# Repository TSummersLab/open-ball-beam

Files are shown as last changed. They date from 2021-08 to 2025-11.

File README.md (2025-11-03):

<div align="center">

</div>

# OBB: Open Ball & Beam

[**Hardware**](#hardware)
| [**Software**](#software)
| [**Mathematics**](#mathematics)
| [**Contributors**](#contributors)

## What is OBB?

OBB is *control science for everyone*.

1. A low-cost, open-source hardware and software platform.
2. For research, teaching, and self-guided instruction in data-driven control.
3. An open-loop neutrally stable dynamical system that is nontrivial to control.

## Why OBB?

[Existing educational control systems](docs/ALTERNATIVES.md) are often

1. Prohibitively expensive (cost thousands of USD)
2. Use proprietary hardware and software
   - Development knowledge is not transferrable to other systems.

OBB offers a viable alternative

1. OBB is cheap enough for most individuals and labs.
2. OBB uses open-source and widely available hardware and software.

OBB encourages users to get their hands dirty!

1. Redesign custom 3D parts
2. Create new & improved controllers
3. Try out reinforcement learning algorithms

# Hardware

## Parts list

See [`parts_list.xlsx`](hardware/parts_list.xlsx) for a list of parts to purchase and to kit out a single OBB unit.

## CAD models

CAD models for 3D printing are provided in the [`cad`](hardware/cad) directory.

- [STEP files](hardware/cad/step) (portable format), suitable for 3D printing.
- [PTC Creo files](hardware/cad/creo) (native format), suitable for viewing and redesign in PTC Creo.
  - The full assembly [`ballbeam.asm`](hardware/cad/creo/ballbeam.asm) may be opened in Creo. Working kinematic joints are provided so the movement can be interacted with via dragging.

## Assembly and setup

See the [Assembly and Setup Guide](docs/OBB_Assembly_and_Setup_Guide/OBB_Assembly_and_Setup_Guide.pdf) for instructions on how to assemble an OBB unit.

<div align="center">
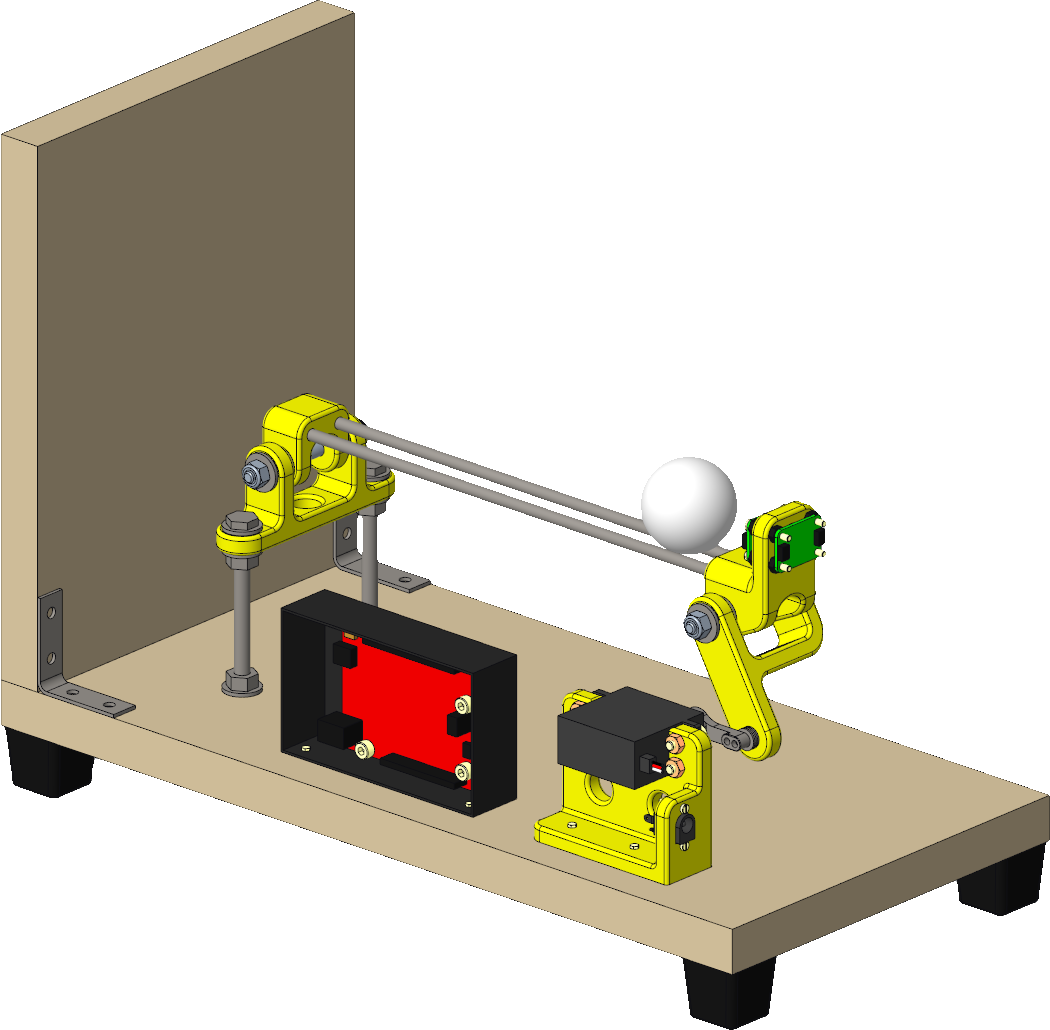
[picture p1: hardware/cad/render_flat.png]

&nbsp; &nbsp; &nbsp; &nbsp;
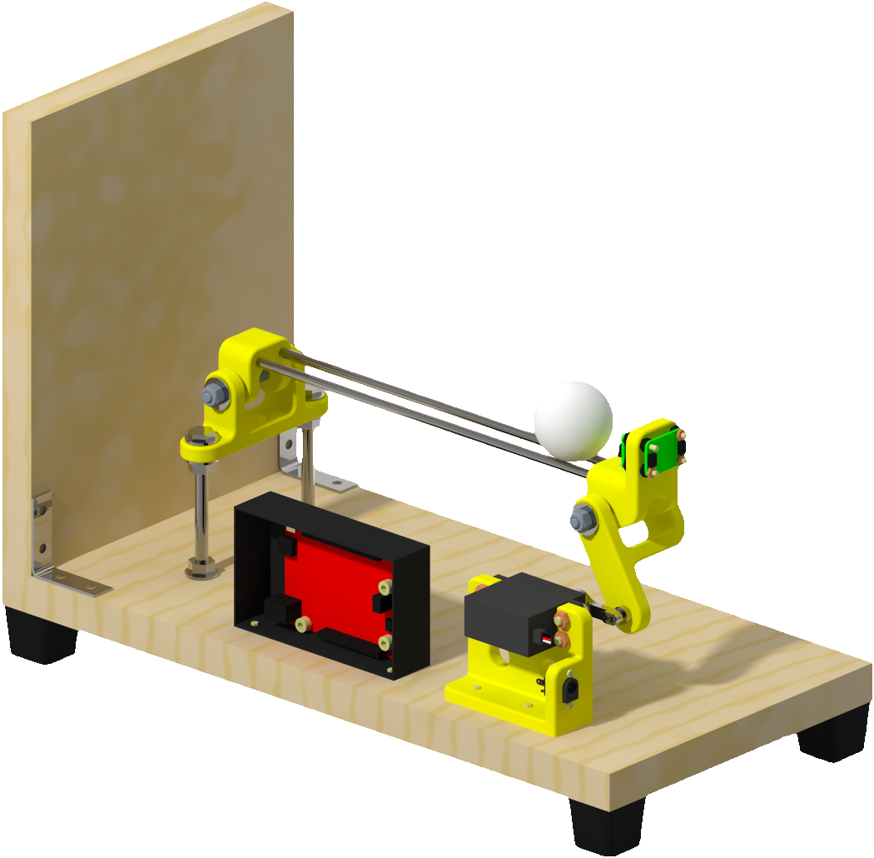
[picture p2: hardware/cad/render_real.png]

&nbsp; &nbsp; &nbsp; &nbsp;
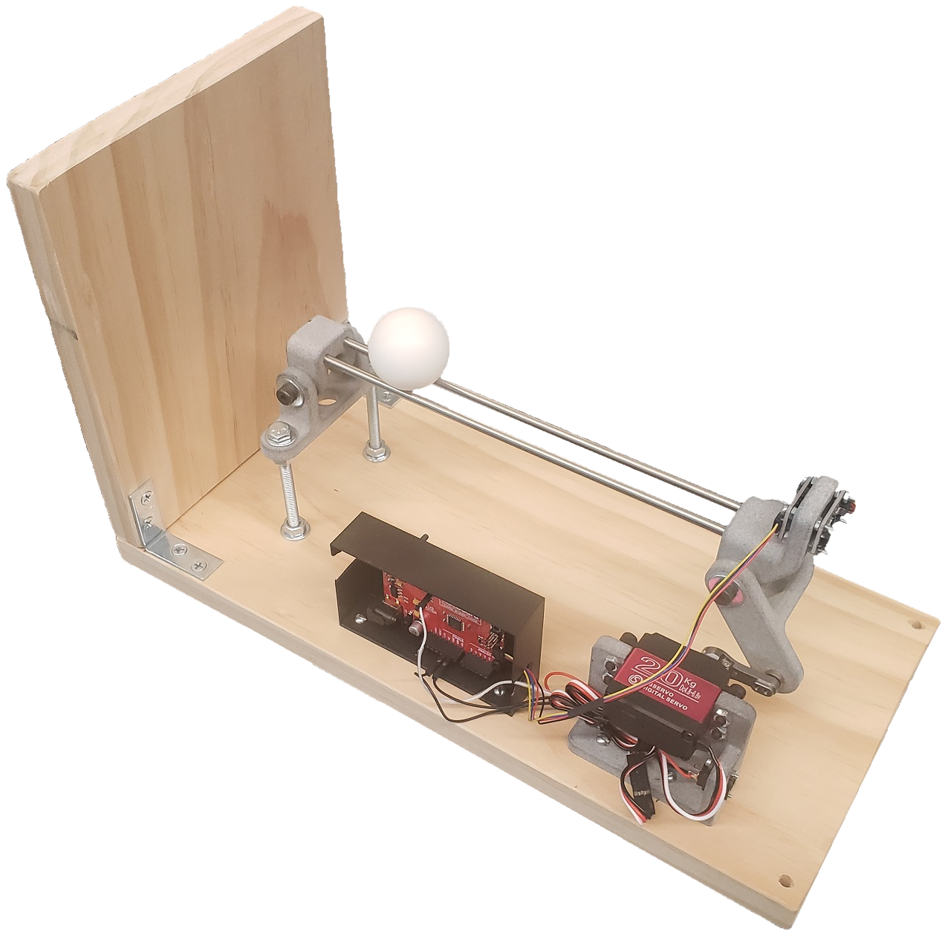
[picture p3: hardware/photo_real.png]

</div>

# Software

## Development info

OBB was developed and tested on 64-bit Windows 10 using Anaconda environments, but should work on other platforms as well e.g. macOS & Linux.

## Features

OBB ships with the following software features.

### Control schemes

- Proportional-integral-derivative (PID)
- Linear quadratic regulator (LQR) with integral control
- Model predictive control (MPC) with integral control
- Anti-windup for integral control

### Observation processing schemes

- Exponential smoothing
- Linear quadratic state estimation (Kalman filter)

### Convenience features

- Ball removal detection

### OpenAI Gym environments

OBB ships with environments compatible with [OpenAI Gym](https://gym.openai.com/) (requires Gym installation)

- Continuous action-space environment `BallBeamContinuousEnv`
- Discrete action-space environment `BallBeamDiscreteEnv`
- Option to use simulator (with fast visualizer) or the actual physical hardware

Try out reinforcement learning algorithms e.g. those from [OpenAI Spinning Up](https://spinningup.openai.com/en/latest/) in simulation or on a real-world physical system!

## Setup

### Arduino

#### Dependencies

- [Arduino IDE](https://www.arduino.cc/en/software)
- [Servo library](https://www.arduino.cc/reference/en/libraries/servo/)
- [Polulu VL53L0X library](https://github.com/pololu/vl53l0x-arduino)
- [Adafruit_LSM6DS](https://github.com/adafruit/Adafruit_LSM6DS)
- [BasicLinearAlgebra](https://www.arduino.cc/reference/en/libraries/basiclinearalgebra/)

1. Install the [Arduino IDE](https://www.arduino.cc/en/software)
2. Install the following libraries from the `Manage Libraries...` dialog in the Arduino IDE
    - [Servo](https://www.arduino.cc/reference/en/libraries/servo/) (may be installed already with the Arduino IDE)
    - [Polulu VL53L0X](https://github.com/pololu/vl53l0x-arduino)
        - Search for `VL53L0X`
        - Be sure to use the Polulu library and NOT the Adafruit Library (regardless of whether the Polulu or the Adafruit physical hardware is used)
    - [Adafruit_LSM6DS](https://github.com/adafruit/Adafruit_LSM6DS)
        - Search for `Adafruit LSM6DS`
        - Select `Install All` if prompted
    - [BasicLinearAlgebra](https://www.arduino.cc/reference/en/libraries/basiclinearalgebra/)
        - Search for `BasicLinearAlgebra`

### Python

It is recommended to use [virtualenv](https://docs.python.org/3/library/venv.html) to create a separate environment to install OBB and its dependencies.

1. Open a terminal / command prompt
2. Create a new environment
3. Activate the desired environment
4. Install the dependency packages
    - ```pip install -r requirements.txt```

#### OBB Installation

1. Navigate to the root level directory of this package.
2. Run the command `pip install -e .`
    - NOTE: The `-e` option is very important! This is what tells pip to install in "editable mode", so that changes you make to scripts actually take effect when you run them! Read the [official pip docs](https://pip.pypa.io/en/stable/topics/local-project-installs/#editable-installs) for more details.

#### Development

##### Pre-commit

Run

```bash
pre-commit run --all-files
```

to run all pre-commit hooks, including style formatting and unit tests.

##### Package management

Update [`requirements.in`](requirements.in) with new direct dependencies.

Then run

```bash
pip-compile requirements.in
```

to update the [`requirements.txt`](requirements.txt) file with all indirect and transitive dependencies.

Then run

```bash
pip install -r requirements.txt
```

to update your virtual environment with the packages.

If necessary, also add the type hints package to the `additional_dependencies` for `mypy` in [`.pre-commit-config.yaml`](.pre-commit-config.yaml) so that `mypy` knows about the type hints (often required for less popular packages).

### General setup (cross-platform Arduino <--> Python)

1. Baud rate
    - A baud rate of 115200 is used throughout the project.
    - When using `Tools` -> `Serial Monitor` or `Serial Plotter` make sure to use 115200 baud rate.

2. COM port
    - Determine the COM port that your Arduino is attached to
        - e.g. use Device Manager in Windows
    - In [`hardware_configurator.py`](ballbeam/configurators/hardware_configurator.py) change `PORT` to `COM#` as appropriate.

3. Servo and sensor calibration coefficients
    - Run [`servo_calibrator.py`](ballbeam/calibrators/servo_calibrator.py) and [`sensor_calibrator.py`](ballbeam/calibrators/sensor_calibrator.py)
    - Copy the printed coefficients into [`constants.cpp`](ballbeam/arduino/interface/src/constants.cpp)

## APIs

There are two APIs that offer comparable functionality:

1. [**Arduino API**](#arduino-api)
2. [**Python API**](#python-api)

### Arduino API

In the Arduino API, all processing (e.g. control and state estimation) occurs locally on the Arduino board. No serial connection to a host computer is strictly required during system operation; a serial connection is required only for uploading programs and for monitoring system operation through the Serial Monitor and Serial Plotter.

The benefit of the Arduino API is that no host computer is required to run the system.
In this configuration, only power to the Arduino (e.g. over the USB cable) is necessary, so the system is more portable and be run from any location with power outlets.
MPC control is currently not available in the Arduino API.

#### Usage

##### Arduino

1. Upload [`interface.ino`](ballbeam/arduino/interface/interface.ino) to the Arduino.
2. Start the `Tools` -> `Serial Plotter` to monitor the various signals in the system.

### Python API

In the Python API, the majority of processing occurs on the host computer and the Arduino acts as a simple client, sending raw measurement information and receiving actuator commands. A stable serial connection is required throughout system operation to maintain stability.

The benefit of the Python API is that the full computing power of the host computer can be used to control the system.
In particular, the more computationally intensive MPC strategy can be used.

#### Setup

In order to use the MPC controller, the solver code must be generated with

```bash
python configurators/controller/mpc/design.py
```

#### Usage

##### Arduino

1. Upload [`client.ino`](ballbeam/arduino/interface/client.ino) to the Arduino.

##### Host computer

1. Adjust all the configurable parameters in the [`*_configurator.py`](ballbeam/configurators) files as needed.
     - Set the `system_type` variable to `'Simulator'` in [`interface_configurator.py`](ballbeam/configurators/interface_configurator.py) first to ensure proper functioning in the simulator before attempting to run on the physical hardware.
2. Run [`python configurators.py`](ballbeam/configurators/configurators.py) to run all configurators.
3. Run [`python main.py`](ballbeam/common/interface.py) to start the interface (without running configurators).
    - Alternatively, run [`python main.py --configure`](ballbeam/main.py) to run the configurators as well as start the interface.

## Mathematics

An technical write-up describing the [mathematics](docs/OBB_Mathematics/OBB_Mathematics.pdf) behind the software is available.
Note that this document is still in development.

# Contributors

- Original author: [Benjamin Gravell](https://github.com/BenGravell)
- Testing and improvements: [Sleiman Safaoui](https://github.com/The-SS) and [Karthik Ganapathy](https://github.com/Klickeazy)

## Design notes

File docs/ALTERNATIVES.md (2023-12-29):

# Alternative Ball & Beam systems

## Quanser Ball and Beam

- Commercial product available from <https://www.quanser.com/products/ball-and-beam/> .
- Price not publicly available, but indications are that the cost runs in the several thousand dollar range. <https://ftp.esat.kuleuven.be/stadius/barrero/cacsd/www%20and%20mails/EDU_Pricing.pdf>
- Proprietary control software, tethered to a company for support and under-the-hood knowledge.

## BOBShield

Recently BOBShield was proposed:

- <https://ieeexplore.ieee.org/abstract/document/9454013>
- <https://github.com/gergelytakacs/AutomationShield/wiki/BoBShield>

Similarities between BOBShield and OBB:

- Arduino-based
- Open-source
- Time-of-flight sensor

Benefits of BOBShield over OBB:

- Smaller
- Lower cost
- Lower part count
- Ball cannot fall off

Drawbacks of BOBShield under OBB:

- Tube/beam length is very small.
  - Limited operational range.
  - Harder to visualize large excursions.
- Servo is directly attached to the beam.
  - Beam angle to servo angle ratio is 1:1, which results in a lack of precision.
  - Beam angle only needs to be +/- 5 degrees in typical operation, while servo can easily do +/- 90 degrees.
  - Servo cannot rotate through its full range without collision.
    - By contrast, OBB the servo can rotate 360 degrees without issue.
    - Good during troubleshooting in case servo is accidentally commanded/activated to large angles.
- Servo is driven by Arduino power rather than an external power source
  - BOBShield can get away with this because they use a micro servo, but not ideal for reliable power delivery
- Ball is captured inside a transparent tube.
  - Can lead to unusual friction behavior (harder to control).
  - ToF sensor not able to function properly due to occlusions (harder to sense).
- No IMU sensor.
  - Cannot automatically calibrate servo angle against Earth's gravity.

## PyMoskito

<https://pymoskito.readthedocs.io/>

- Purely a software package.
- Has a Ball & Beam model <https://pymoskito.readthedocs.io/en/stable/examples/ballbeam.html>
- Also has several other dynamical systems.

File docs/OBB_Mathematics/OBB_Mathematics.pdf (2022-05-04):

# OBB: Open Ball & Beam Mathematics

### Contents

1 Model | 2
2 Control | 4
3 State estimation | 5

1

### 1 Model

The dynamics of the ball-and-beam are modeled as follows, according to a simplified development of [1–3]. Define the model constants

Quantity | Expression
Gravitational acceleration | g
Damping coefficient | d

Define the model coordinates

Quantity | Expression
Position of the ball along the beam | p
Beam angle | θ
Weight force | W = mg
Damping force | D = dp˙

Define the system quantities

Quantity | Expression
State | x = [p p˙]

⊺
Input | u = sin(θ)
Output | y = p

A basic model¹
can be derived using Newtonian or Lagrangian mechanics:
m +

J
R²
p¨ = −W sin θ − D | (1)
= −mg sin θ − dp˙ | (2)

Define the scaling factor

c =

m +

J
R²
m

= 1 +

J
mR²
, | (3)

which has the effect of reducing the effect of gravity on the acceleration of the ball depending on the rotational inertia of the ball. Assuming a solid spherical ball,

c = 1 +

2
5mR²
mR²

= 1 +

2
5
= 1.4 | (4)

Using the scaling constant,

mcp¨ = −mg sin θ − dp˙ | (5)

Rearranging,

p¨ = −

g
c

sin θ −

d
mc
p˙ | (6)

Using the system quantities, we obtain the linear continuous-time model

x˙ =

0 1
0 − d
mc
x +
0
−

g
c
u, | (7)

y =

0 1
x. (8)

1These dynamics ignore certain higher-order terms, see [3].
2

### 1.1 Discretization

TODO discretization to obtain a discrete-time from the continuous-time one

### 1.2 Disturbance modeling

TODO introducing additive process and measurement noise we obtain the stochastic state-input-output model

### 1.3 Integral control

TODO state augmentation for input difference penalization

### 1.4 Control input difference penalization

TODO state augmentation for integral control

### 1.5 Linearization of servo actuation and sensor readings

Due to the mechanical linkage and possibly other sources, there is a nonlinear relation between the PWM signal given to the servo motor and the angle of the beam.
Due to variations in the reflected light from the ball as it travels away from the ToF sensor, there is a nonlinear relation between the sensor reading and the actual physical distance of the ball from the sensor. These are both dealt with by fitting polynomials to collected data using least-squares. This is part of the calibration procedure.
The nonlinear transform to convert from an action u to a raw PWM signal for the servo is given by
PWM = poly(u) | (9)

The nonlinear transform to convert from a raw sensor reading to an observation y is given by

y = poly(reading) | (10)

In particular, degree-5 polynomials are used.

3

### 2 Control

### 2.1 Proportional-integral-derivative (PID)

TODO

### 2.2 Linear-quadratic regulator (LQR)

TODO

### 2.3 Model-predictive control (MPC)

TODO

4

### 3 State estimation

### 3.1 Exponential filtering

TODO

### 3.2 Optimal linear-quadratic estimation (LQE) / Kalman filtering (KF)

TODO

### 3.3 Extended Kalman filter (EKF)

TODO

### 3.4 Unscented Kalman filter (UKF)

TODO

### 3.5 Particle filter (PF)

TODO

### References

[1] D. Morin, The Lagrangian method, p. 218–280. Cambridge University Press, 2008.
[2] C. G. Bol´ıvar-Vincenty and G. Beauchamp-Baez, “Modelling the ball-and-beam system from Newtonian ´ mechanics and from Lagrange methods,” in Twelfth LACCEI Latin American and Caribbean Conference for Engineering and Technology, vol. 22, p. 24, 2014.
[3] J. Hauser, S. Sastry, and P. Kokotovic, “Nonlinear control via approximate input-output linearization: the ball and beam example,” IEEE Transactions on Automatic Control, vol. 37, no. 3, pp. 392–398, 1992.

5

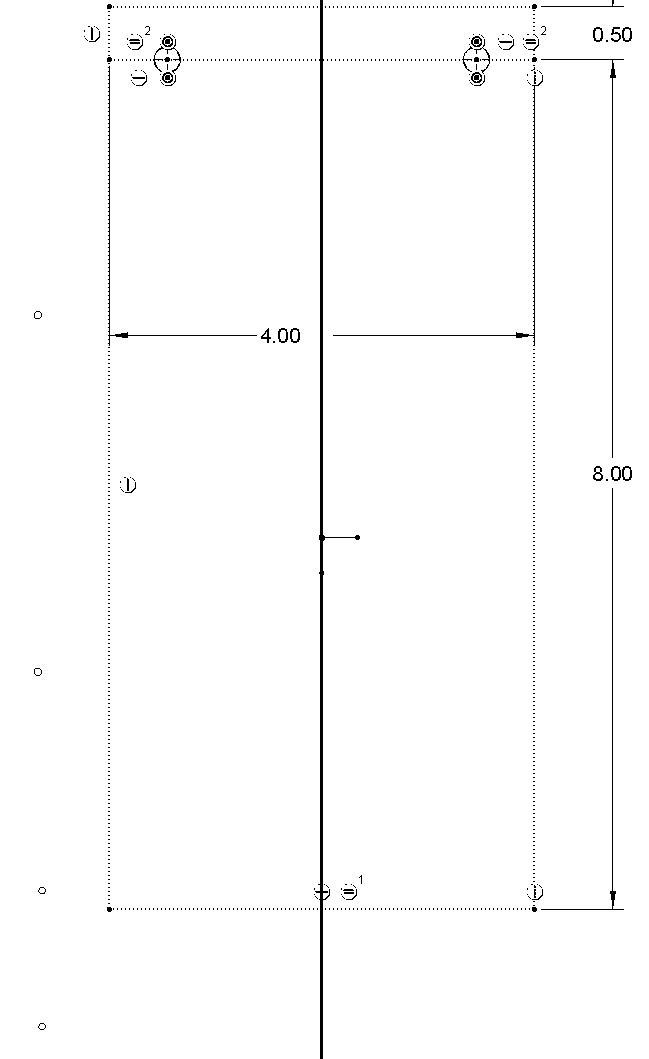
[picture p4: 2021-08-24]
hardware/base_template.jpg

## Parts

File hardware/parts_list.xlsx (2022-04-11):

Short name | Long description | Notes | Vendor | Part Number | Link | Qty. (assy) | Qty. (purchase) | Unit price | Total price | Subassy | Type
IMU sensor | Adafruit LSM6DS33 6-DoF Accel + Gyro IMU - STEMMA QT / Qwiic |  | Adafruit | 4480 | https://www.adafruit.com/product/4480 | 1 | 1 | $5.95 | $5.95 | Beam | Electronic
ToF sensor | Adafruit VL53L0X Time of Flight Distance Sensor |  | Adafruit | 3317 | https://www.adafruit.com/product/3317 | 1 | 1 | $14.95 | $14.95 | Beam | Electronic
Jumper wire | Premium Male/Male Jumper Wires - 20 x 6" (150mm) |  | Adafruit | 1957 | https://www.adafruit.com/product/1957 | 4 | 1 | $1.95 | $1.95 | Servo cluster | Electronic
Micro USB cable | USB cable - USB A to Micro-B - 3 foot long |  | Adafruit | 592 | https://www.adafruit.com/product/592 | 1 | 1 | $2.95 | $2.95 | Arduino cluster | Electronic
Qwiic cable 200mm | Qwiic cable 200mm length | ToF sensor to ardiuno | Adafruit | 4401 | https://www.adafruit.com/product/4401 | 1 | 1 | $0.95 | $0.95 | Arduino cluster | Electronic
Qwiic cable 50mm | Qwiic cable 50mm length | ToF sensor to IMU sensor | Adafruit | 4399 | https://www.adafruit.com/product/4399 | 1 | 1 | $0.95 | $0.95 | Beam | Electronic
Servo | ANNIMOS 20KG Digital Servo DS3218MG | Comes with a servo horn (has two screws in it pre-installed) and a screw | Amazon | B076CNKQX4 | https://www.amazon.com/ANNIMOS-Digital-Waterproof-DS3218MG-Control/dp/B076CNKQX4 | 1 | 1 | $16.66 | $16.66 | Servo cluster | Electronic
Rail | 5mm diameter x 250mm length stainless steel rod (5x pieces) |  | Amazon | g20080400ux0010 | https://www.amazon.com/gp/product/B082ZNJR7D | 2 | 1 | $8.99 | $8.99 | Beam | Structural
Fork | Fork, 3D printed, MJF Nylon PA12 Raw (Solid Gray) | Connects servo and sensor mounts | CraftCloud | N/A | https://craftcloud3d.com/ | 1 | 1 | $10.82 | $10.82 | Beam | Structural
Hinge | Hinge, 3D printed, MJF Nylon PA12 Raw (Solid Gray) | Near the back board | CraftCloud | N/A | https://craftcloud3d.com/ | 1 | 1 | $11.96 | $11.96 | Base | Structural
Rail holder base | Rail holder, 3D printed, MJF Nylon PA12 Raw (Solid Gray) | Attaches to the hinge, holds the rail | CraftCloud | N/A | https://craftcloud3d.com/ | 1 | 1 | $6.14 | $6.14 | Beam | Structural
Rail holder tip | Sensor mount, 3D printed, MJF Nylon PA12 Raw (Solid Gray) | Holds the sensors | CraftCloud | N/A | https://craftcloud3d.com/ | 1 | 1 | $12.15 | $12.15 | Beam | Structural
Servo mount | Servo mount, 3D printed, MJF Nylon PA12 Raw (Solid Gray) | Holds the servo | CraftCloud | N/A | https://craftcloud3d.com/ | 1 | 1 | $19.17 | $19.17 | Servo cluster | Structural
Barrel jack | 2.1mm ID, 5.5mm OD barrel jack panel mount | Powers the servo only | Digikey | CP-038AH-ND | https://www.digikey.com/en/products/detail/cui-devices/PJ-038AH/1644551 | 1 | 1 | $0.73 | $0.73 | Servo cluster | Electronic
Power supply | 5V power supply L6R12H-050 |  | Digikey | 364-1261-ND | https://www.digikey.com/en/products/detail/tri-mag-llc/L6R12H-050/7682624 | 1 | 1 | $7.60 | $7.60 | Servo cluster | Electronic
#6 x 5/8" wood screw | #6-18 x 5/8" Phillips Round Head Wood Screw, Zinc | Phillips or Slot head style is OK, hold the Arduino enclosure and the servo mount to the base board | Fastenal | 30560 | https://www.fastenal.com/products/details/30560 | 4 | 4 | $0.05 | $0.22 | Base | Fastener
Corner brace | 1-1/2" x 5/8" Zinc Boxed Corner Brace Without Screws | Hold the two wood boards (with the corner brace) | Fastenal | 129758 | https://www.fastenal.com/product/hardware/braces-and-brackets/equipment-braces?categoryId=600211&level=3&query=129758&isExpanded=true | 2 | 2 | $1.22 | $2.44 | Base | Fastener
#8 x 3/4" wood screw | #8-15 x 3/4" Flat Countersunk Head Phillips Drive Sharp Point Zinc Finish Wood Screw |  | Fastenal | 30124 | https://www.fastenal.com/products/details/30124 | 8 | 8 | $0.07 | $0.53 | Base | Fastener
1/4" bolt | 1/4"-20 x 4" SAE J429 Grade 5 Zinc Finish Steel Tap Bolt | Upright support for the hinge | Fastenal | 144479 | https://www.fastenal.com/products/details/0144479 | 2 | 2 | $0.58 | $1.16 | Base | Fastener
1/4" nut | 1/4"-20 Zinc Finish Grade 5 Finished Hex Nut | Upright support for the hinge | Fastenal | 36302 | https://www.fastenal.com/products/details/36302 | 6 | 6 | $0.05 | $0.32 | Base | Fastener
#10 lock nut | #10-24 Grade 2 Zinc Finish NM Steel Nylon Insert Lock Nut | Used to lock the rail holder sholder bolts (between the rail holders and the hinge and fork respectively) | Fastenal | 37014 | https://www.fastenal.com/products/details/37014 | 2 | 2 | $0.06 | $0.11 | Beam | Fastener
1/4" shoulder bolt | Alloy Steel Shoulder Screw, 1/4" Shoulder Diameter, 2" Shoulder Length, 10-24 Thread |  | Fastenal | 26310 | https://www.fastenal.com/product?query=26310&fsi=1 | 2 | 2 | $2.29 | $4.58 | Beam | Fastener
1/4" washer | 1/4" x 0.625" OD Low Carbon Zinc Finish Steel SAE General Purpose Flat Washer | For the 1/4" bolt and the 1/4" shoulder bolt | Fastenal | 1133078 | https://www.fastenal.com/product?query=1133078&fsi=1 | 16 | 16 | $0.05 | $0.84 | Various | Fastener
M2 nut | M2-0.4 DIN 934 Plain Finish Steel Class 6 Hex Nut | For barrel jack | Fastenal | 40140 | https://www.fastenal.com/product?query=40140&fsi=1 | 2 | 2 | $0.04 | $0.07 | Servo cluster | Fastener
M2 x 12mm bolt | M2-0.4 x 12mm ISO 4762/DIN 912 Hex Drive Class 12.9 Zinc Finish Alloy Steel Socket Cap Screw | For barrel jack | Fastenal | 141685 | https://www.fastenal.com/product?query=0141685&fsi=1 | 2 | 2 | $0.22 | $0.44 | Servo cluster | Fastener
M2.5 nut | M2.5-0.45 DIN 934 Zinc Finish Steel Class 6 Hex Nut | For IMU/dist sensor | Fastenal | 40301 | https://www.fastenal.com/product?query=40301&fsi=1 | 11 | 8 | $0.14 | $1.12 | Beam | Fastener
M2.5 x 20mm bolt | M2.5-0.45 x 20mm DIN 7985 Phillips Drive Pan Head Zinc Finish Steel Machine Screw | For IMU/dist sensor | Fastenal | 91182 | https://www.fastenal.com/product?query=91182&fsi=1 | 4 | 4 | $0.12 | $0.49 | Beam | Fastener
M3 nut | M3-0.5 DIN 934 Zinc Finish Steel Class 8 Hex Nut | For the arduino | Fastenal | 1140302 | https://www.fastenal.com/product?query=1140302&fsi=1 | 4 | 4 | $0.04 | $0.18 | Arduino cluster | Fastener
M3 x 12mm bolt | M3-0.5 x 12mm ISO 4762 Hex Drive Class 12.9 Black Oxide Finish Alloy Steel Socket Cap Screw | For the arduino | Fastenal | 39505 | https://www.fastenal.com/products/details/39505 | 4 | 4 | $0.21 | $0.82 | Arduino cluster | Fastener
M3 standoff | M3 x 6mm female-female standoff | For the arduino, 4.5mm not 6mm | McMaster Carr | 95947A002 | https://www.mcmaster.com/catalog/127/3535 | 4 | 4 | $0.53 | $2.12 | Arduino cluster | Fastener
M4 nut | M4-0.7 DIN 934 Zinc Finish Steel Class 8 Hex Nut | For servo | Fastenal | 1140303 | https://www.fastenal.com/product?query=1140303&fsi=1 | 4 | 4 | $0.05 | $0.21 | Servo cluster | Fastener
M4 washer | M4 washer 4mm ID, 0.8mm thickness | For servo | Fastenal | 40353 | https://www.fastenal.com/products/details/40353 | 4 | 5 | $0.03 | $0.15 | Beam | Fastener
M4 x 16mm bolt | M4-0.7 x 16mm ISO 4762 Hex Drive Class 12.9 Black Oxide Finish Alloy Steel Socket Cap Screw | For servo | Fastenal | 1139526 | https://www.fastenal.com/product?query=1139526&fsi=1 | 4 | 4 | $0.11 | $0.46 | Servo cluster | Fastener
Rubber foot | 352-10-15-M4-S-55 GN352-10-15-M4-S-55 RUBBER BUMPER |  | Fastenal | 99443033 | https://www.fastenal.com/product?query=99443033&fsi=1 | 4 | 4 | $1.29 | $5.16 | Base | Fastener
T-nut | M4 Zinc Finish Low Carbon Steel T-Nut | Hold rubber feet | Fastenal | 11115602 | https://www.fastenal.com/product?query=11115602&fsi=1 | 4 | 4 | $0.35 | $1.38 | Base | Fastener
Wood board | 1" nominal / 0.75" true thickness x 8" nominal / 7.25" true width x 8ft select pine wood board | Both the base board and the back board are cut from this board | Home Depot | 202535862 | https://www.homedepot.com/p/1-in-x-8-in-x-8-ft-Select-Pine-Board-929612/202535862 | 2 | 1 | $6.12 | $6.12 | Base | Structural
4 mm shoulder bolt | Alloy Steel Shoulder Screw, 4 mm Shoulder Diameter, 12 mm Shoulder Length, M3 x 0.5 mm Thread | Connects servo arm to the fork | McMaster Carr | 92981A143 | https://www.mcmaster.com/catalog/127/3338/ | 1 | 1 | $2.82 | $2.82 | Beam | Fastener
Ball | Delrin Acetal Resin Ball, 1.5 inch diameter |  | McMaster Carr | 9614K39 | https://www.mcmaster.com/plastic-balls/wear-resistant-easy-to-machine-delrin-acetal-resin-balls/ | 1 | 1 | $3.58 | $3.58 | Beam | Structural
Enclosure | Potting box, 3-15/16" x 2-3/8" x 1" 1040N23 |  | McMaster Carr | 1040N23 | https://www.mcmaster.com/catalog/127/981 | 1 | 1 | $5.79 | $5.79 | Arduino cluster | Structural
Arduino | SparkFun Redboard Qwiic |  | SparkFun | 15123 | https://www.sparkfun.com/products/15123 | 1 | 1 | $19.95 | $19.95 | Arduino cluster | Electronic
TOTAL |  |  |  |  |  |  | 111 |  | $182.99

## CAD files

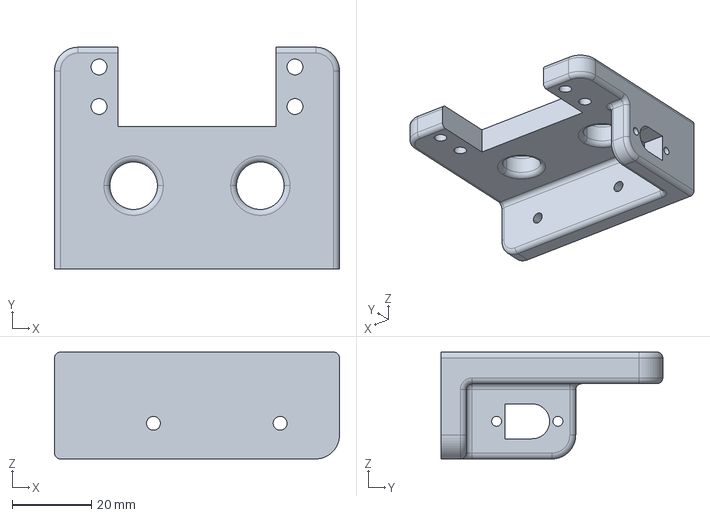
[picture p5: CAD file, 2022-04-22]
hardware/cad/step/servo_mount.stp
72.0 x 56.0 x 27.0 mm

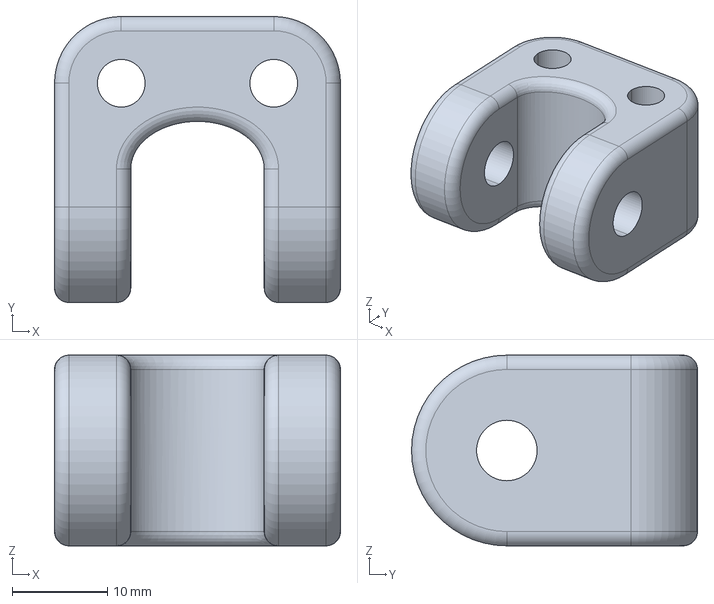
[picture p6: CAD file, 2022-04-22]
hardware/cad/step/rail_holder_base.stp
30.0 x 30.0 x 20.0 mm

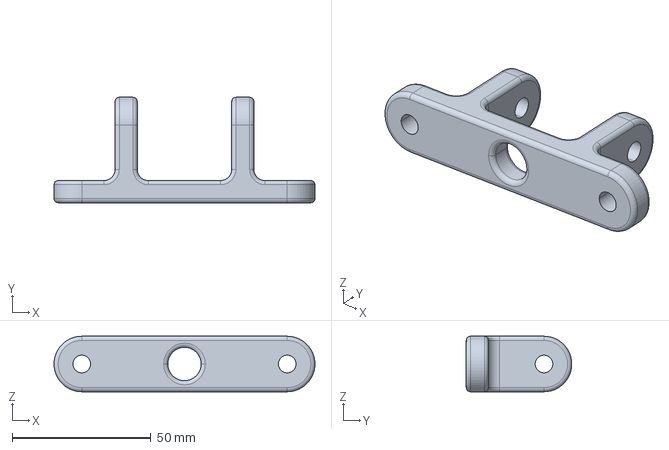
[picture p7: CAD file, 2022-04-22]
hardware/cad/step/base_hinge_fork.stp
94.0 x 38.0 x 20.0 mm

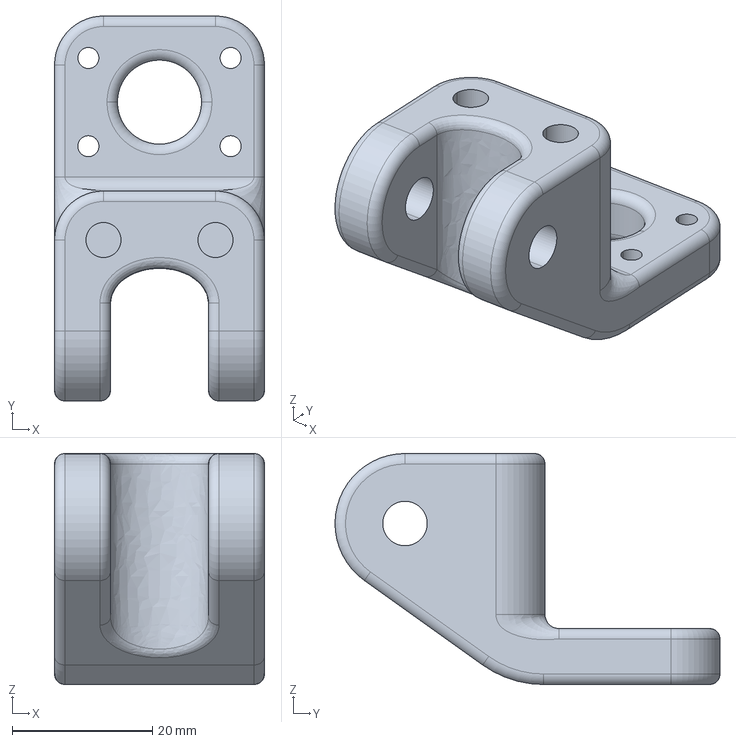
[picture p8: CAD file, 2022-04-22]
hardware/cad/step/rail_holder_tip.stp
30.0 x 55.0 x 33.0 mm

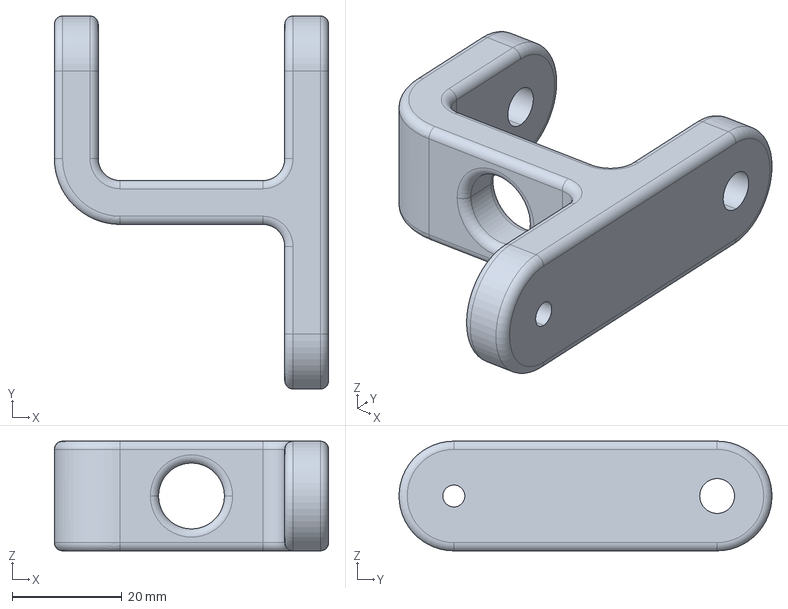
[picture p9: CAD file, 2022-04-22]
hardware/cad/step/fork.stp
50.0 x 68.0 x 20.0 mm

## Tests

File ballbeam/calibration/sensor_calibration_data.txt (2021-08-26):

Sensor calibration

BEGIN DATA COLLECTION
True distance 14
26
27
31
29
24
24
32
30
33
29
27
25
29
25
27
29
24
28
34
29

True distance 30
53
46
50
50
46
50
43
45
47
54
47
47
49
49
46
47
46
48
47
46

True distance 40
56
58
58
58
55
54
60
59
60
58
61
62
62
57
63
58
61
62
63
58

True distance 50
71
75
78
72
72
70
75
70
70
73
72
72
73
70
73
71
73
70
73
67

True distance 60
78
85
80
84
80
83
80
86
82
82
83
83
82
79
86
87
86
83
77
85

True distance 70
89
90
85
93
91
94
90
95
89
92
89
97
92
92
92
91
94
93
93
92

True distance 80
98
102
104
104
105
102
101
105
106
106
102
109
103
109
105
104
105
103
100
104

True distance 90
119
121
118
118
116
117
116
117
119
119
113
118
119
115
117
117
116
118
119
116

True distance 100
132
129
135
136
132
135
133
131
132
134
133
132
134
136
137
131
132
136
133
132

True distance 105
141
143
143
143
138
143
139
145
142
142
139
145
140
141
144
148
141
145
140
144

True distance 110
152
148
157
154
155
155
152
152
152
155
151
153
157
156
153
155
154
152
152
153

True distance 120
176
171
178
170
179
174
175
173
178
177
177
174
173
174
173
170
179
172
172
173

True distance 130
201
202
203
202
202
208
200
198
205
204
205
197
204
200
198
199
205
197
199
203

True distance 140
220
223
220
221
223
219
215
218
223
225
219
220
226
220
224
224
219
222
220
218

True distance 150
240
241
240
244
241
240
241
243
241
243
243
244
239
240
243
239
239
238
246
238

True distance 160
256
253
256
254
259
254
256
262
253
254
258
259
256
259
253
259
259
253
256
260

True distance 170
269
269
272
270
270
268
270
270
267
267
265
270
270
267
271
266
264
267
271
263

True distance 196
282
289
287
291
290
292
289
285
287
292
290
293
289
291
293
289
289
292
289
287

END DATA COLLECTION

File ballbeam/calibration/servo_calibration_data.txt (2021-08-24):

Servo angle calibration
LSM6DS33 Found!
Accelerometer range set to: +-2G
Accelerometer data rate set to: 26 Hz

BEGIN DATA COLLECTION
1000
9.571889 -0.094517 1.366900
9.567104 -0.090927 1.355534
9.560523 -0.095115 1.351347
9.565907 -0.099900 1.359721
9.558131 -0.087936 1.364507
9.563515 -0.095713 1.358525
9.576077 -0.084347 1.363909
9.561719 -0.098106 1.368096
9.573085 -0.090927 1.359721
9.565309 -0.089731 1.351347
9.569497 -0.086740 1.355534
9.571291 -0.084945 1.357927
9.568301 -0.079561 1.356730
9.568301 -0.095115 1.357927
9.567104 -0.075972 1.348954
9.567104 -0.089731 1.353739
9.567104 -0.095115 1.357329
9.562916 -0.096909 1.366302
9.567104 -0.080758 1.362712
9.562916 -0.086740 1.353739

1100
9.583853 -0.086142 1.159921
9.560523 -0.098704 1.182653
9.570095 -0.151944 1.162314
9.613763 -0.053839 1.149751
9.588041 -0.099900 1.168894
9.585050 -0.104686 1.169492
9.582059 -0.098704 1.158126
9.555140 -0.123230 1.177867
9.586247 -0.105882 1.164706
9.635299 -0.023928 1.143769
9.614362 -0.090927 1.144367
9.566505 -0.125623 1.172483
9.569497 -0.099900 1.155135
9.567104 -0.067597 1.168894
9.587443 -0.111266 1.153341
9.588041 -0.116052 1.143171
9.580862 -0.068794 1.165903
9.593425 -0.074776 1.155135
9.637094 -0.045464 1.149153
9.554541 -0.133400 1.165903

1200
9.607184 -0.084347 0.908674
9.607782 -0.069392 0.920040
9.621541 -0.079561 0.904487
9.614362 -0.076570 0.908076
9.615559 -0.069990 0.918844
9.626326 -0.079561 0.918246
9.606585 -0.078365 0.913460
9.619148 -0.065803 0.918844
9.604193 -0.086142 0.911665
9.604790 -0.097508 0.911665
9.612566 -0.077767 0.902692
9.604790 -0.087936 0.908076
9.611969 -0.087338 0.909273
9.617951 -0.078963 0.904487
9.610773 -0.082552 0.911067
9.617353 -0.061615 0.909871
9.608380 -0.077169 0.913460
9.611969 -0.080758 0.909871
9.613763 -0.076570 0.902094
9.602996 -0.083749 0.906880

1300
9.629916 -0.073579 0.639482
9.622138 -0.110070 0.619143
9.631112 -0.066401 0.623330
9.628121 -0.069392 0.625723
9.631710 -0.065803 0.625125
9.623933 -0.068794 0.635893
9.637692 -0.072383 0.619143
9.606585 -0.125025 0.623330
9.621541 -0.091525 0.625125
9.623335 -0.080160 0.626920
9.638291 -0.052642 0.626321
9.625728 -0.087338 0.616152
9.625728 -0.068794 0.622732
9.632906 -0.059222 0.619741
9.629317 -0.075374 0.625723
9.632308 -0.074178 0.623929
9.626924 -0.074776 0.623330
9.631112 -0.072981 0.613759
9.616754 -0.062213 0.622732
9.631710 -0.077767 0.616750

1400
9.638291 -0.068195 0.330808
9.632308 -0.074776 0.334397
9.634103 -0.072383 0.327817
9.640085 -0.065803 0.329611
9.641880 -0.066401 0.321236
9.634700 -0.071785 0.330808
9.634103 -0.066401 0.328415
9.637094 -0.074776 0.321236
9.638291 -0.075374 0.326620
9.641880 -0.068794 0.326022
9.636496 -0.069392 0.325424
9.663414 -0.041874 0.322433
9.646665 -0.055035 0.327219
9.643673 -0.071186 0.321236
9.634700 -0.060419 0.324826
9.641282 -0.066401 0.334995
9.643075 -0.056231 0.324826
9.643673 -0.057428 0.339781
9.644272 -0.065204 0.325424
9.637692 -0.066401 0.337986

1500
9.637094 -0.062213 0.068195
9.637692 -0.063410 0.060419
9.640085 -0.059222 0.066401
9.637094 -0.068794 0.063410
9.641282 -0.053240 0.061017
9.630513 -0.058026 0.067597
9.642478 -0.058624 0.061017
9.634103 -0.067597 0.066401
9.638888 -0.062213 0.066401
9.636496 -0.060419 0.071186
9.632906 -0.059222 0.057428
9.644870 -0.061615 0.065803
9.634103 -0.056830 0.057428
9.640085 -0.062812 0.062213
9.635897 -0.065204 0.060419
9.638291 -0.054437 0.062812
9.637692 -0.065803 0.059222
9.641282 -0.062213 0.053240
9.632308 -0.070588 0.056231
9.637094 -0.063410 0.050847

1600
9.635299 -0.058624 -0.192622
9.629916 -0.066401 -0.193220
9.628719 -0.056231 -0.192024
9.628719 -0.060419 -0.178265
9.628121 -0.057428 -0.185444
9.638888 -0.057428 -0.180658
9.628719 -0.061017 -0.192024
9.636496 -0.062812 -0.191426
9.637094 -0.059222 -0.195613
9.639487 -0.050847 -0.183649
9.629916 -0.050847 -0.194417
9.629916 -0.052642 -0.186640
9.626924 -0.070588 -0.193220
9.601202 -0.073579 -0.195613
9.631112 -0.049651 -0.173480
9.614960 -0.087936 -0.166899
9.641282 -0.040678 -0.185444
9.653843 -0.047856 -0.189033
9.649657 -0.046062 -0.181855
9.631710 -0.068195 -0.212363

1700
9.585050 -0.078963 -0.370289
9.605388 -0.084347 -0.380459
9.616754 -0.063410 -0.377468
9.644272 -0.044267 -0.378664
9.638291 -0.045464 -0.384646
9.652049 -0.035892 -0.387637
9.639487 -0.032901 -0.368495
9.655040 -0.026321 -0.377468
9.661620 -0.004187 -0.371486
9.621541 -0.067597 -0.382253
9.595818 -0.093320 -0.372084
9.613165 -0.052642 -0.355932
9.586844 -0.105882 -0.367298
9.616157 -0.059222 -0.370289
9.631112 -0.047856 -0.369093
9.582059 -0.088534 -0.360718
9.636496 -0.053240 -0.379861
9.622736 -0.057428 -0.367298
9.640085 -0.046660 -0.368495
9.604790 -0.069392 -0.376870

1800
9.616157 -0.057428 -0.495314
9.613763 -0.047856 -0.490529
9.615559 -0.053839 -0.501296
9.614362 -0.044865 -0.489332
9.604790 -0.044865 -0.496511
9.615559 -0.044267 -0.503091
9.609576 -0.042473 -0.501296
9.613165 -0.053240 -0.489930
9.620345 -0.047258 -0.491127
9.610175 -0.052642 -0.498904
9.613165 -0.053240 -0.487538
9.611371 -0.061017 -0.502493
9.615559 -0.055035 -0.497707
9.610175 -0.053240 -0.494716
9.608978 -0.049651 -0.491725
9.609576 -0.054437 -0.492323
9.621541 -0.054437 -0.492323
9.619148 -0.055035 -0.492921
9.612566 -0.058026 -0.488734
9.592826 -0.063410 -0.492323

1900
9.610175 -0.043669 -0.558126
9.600603 -0.052044 -0.561117
9.616157 -0.059821 -0.565903
9.607782 -0.049053 -0.555135
9.610773 -0.052642 -0.565903
9.613165 -0.040080 -0.566501
9.612566 -0.049651 -0.553340
9.608380 -0.062213 -0.572483
9.605388 -0.040678 -0.556929
9.608978 -0.055035 -0.555733
9.606585 -0.043071 -0.565304
9.610773 -0.051446 -0.566501
9.604790 -0.040080 -0.561715
9.605987 -0.047258 -0.564706
9.608380 -0.044865 -0.566501
9.613165 -0.061017 -0.556331
9.614960 -0.055633 -0.584447
9.594621 -0.056830 -0.568295
9.667004 -0.022732 -0.574876
9.612566 -0.069990 -0.577268

2000
9.597014 -0.051446 -0.608973
9.607184 -0.047856 -0.598206
9.598809 -0.038883 -0.594018
9.602398 -0.049053 -0.586242
9.600603 -0.047856 -0.598804
9.602398 -0.040080 -0.603590
9.614960 -0.053240 -0.595215
9.601799 -0.057428 -0.601795
9.631112 -0.034098 -0.600598
9.595818 -0.035294 -0.597009
9.616754 -0.043071 -0.591027
9.585648 -0.062812 -0.594018
9.595219 -0.058026 -0.595813
9.606585 -0.051446 -0.592822
9.612566 -0.045464 -0.598804
9.604193 -0.047258 -0.603590
9.603594 -0.072383 -0.597009
9.598211 -0.054437 -0.605982
9.607184 -0.052044 -0.601197
9.607184 -0.043669 -0.603590

END DATA COLLECTION

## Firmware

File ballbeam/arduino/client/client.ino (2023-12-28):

#include <Wire.h>
#include <VL53L0X.h>
#include <Servo.h>

VL53L0X sensor;  // Create sensor object
Servo servo;  // Create servo object

const int SERVO_PIN = 10;
const unsigned long BAUD_RATE = 115200;
const byte INT_SIZE = sizeof(int);

// for ANNIMOS DS3218MG
const int SERVO_CMD_MID = 1500;  // in microseconds
const int SERVO_CMD_MIN = SERVO_CMD_MID - 500;  // in microseconds
const int SERVO_CMD_MAX = SERVO_CMD_MID + 500;  // in microseconds
const int SERVO_CMD_REST = SERVO_CMD_MID + 50;  // in microseconds  // make the ball roll down to the end near sensor in the rest state
const int DT = 20;               // in milliseconds

unsigned long now = millis();
unsigned long last = now;
int time_since_last = 0;


void setup() {
  delay(50);
  Wire.begin();             // Begin I2C communication
  delay(50);
  Serial.begin(BAUD_RATE);  // Begin serial connection
  delay(50);

  sensor.setTimeout(250);
  while (!sensor.init()) {
    Serial.println("Failed to detect and initialize sensor VL53L0X!");
    delay(1000);
    }

  // Set sensor timing budget, in microseconds (20000 is the minimum)
  sensor.setMeasurementTimingBudget(20000);
  sensor.startContinuous();

  servo.attach(SERVO_PIN);  // Attach servo object
  servo.writeMicroseconds(SERVO_CMD_REST);
  delay(50);
}


void loop() {
  now = millis();
  time_since_last = now - last;
  if (time_since_last >= DT) {
    // Take a sensor reading
    int reading = sensor.readRangeContinuousMillimeters();

    // Write sensor reading to serial
    Serial.println(reading);

    // Read servo command from serial
    int servo_cmd = read_int();

    // Fail safe to ensure servo pwm is always in the safe range
    servo_cmd = constrain(servo_cmd, SERVO_CMD_MIN, SERVO_CMD_MAX);

    // Issue command to servo
    servo.writeMicroseconds(servo_cmd);

    // Store last time
    last = now;
  }
  else
    delayMicroseconds(1);
}


int read_int() {
  int val;
  unsigned char serial_buffer[INT_SIZE];
  if (Serial.readBytes(serial_buffer, INT_SIZE) == INT_SIZE)
    memcpy(&val, serial_buffer, INT_SIZE);
  else
    val = SERVO_CMD_REST;
  return val;
}

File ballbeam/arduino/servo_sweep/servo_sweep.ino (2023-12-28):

#include <Servo.h>

Servo servo;

const int SERVO_PIN = 10;
const unsigned long BAUD_RATE = 115200;

const float frequency = 0.1;  // in Hz

unsigned long initial_time = millis();
unsigned long now = initial_time;
unsigned long last = initial_time;
long time_since_last = 0;
long time_since_begin = 0;

const int SERVO_CMD_MIN = 500;  // in microseconds
const int SERVO_CMD_MAX = 2500;  // in microseconds

const int DT = 20;               // in milliseconds

double x;
long y;
long servo_out;

void setup() {
  Serial.begin(BAUD_RATE);
  servo.attach(SERVO_PIN);
}

void loop() {
  now = millis();
  time_since_last = now - last;
  if (time_since_last >= DT){
    Serial.print(time_since_last);
    Serial.print(" ");
    time_since_begin = now - initial_time;
    x = sin(2*PI*frequency*time_since_begin/1000);
    y = 1000*x;
    servo_out = map(y, -1000, 1000, SERVO_CMD_MIN, SERVO_CMD_MAX);
    Serial.println(servo_out);
    servo.writeMicroseconds(servo_out);
    last = now;
  }
  else{
    delay(1);
  }
}

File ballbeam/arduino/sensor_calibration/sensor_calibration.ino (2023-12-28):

#include <Wire.h>
#include <VL53L0X.h>
#include <Servo.h>

VL53L0X sensor;  // Create sensor object
Servo servo;  // Create servo object

const int SERVO_PIN = 10;
const unsigned long BAUD_RATE = 115200;
const byte INT_SIZE = sizeof(int);

const int SERVO_CMD_REST = 1400;  // in microseconds  // make the ball roll down to the end near sensor in the rest state
const int DT = 20;               // in milliseconds

const int dists[] = {14, 30, 40, 50, 60, 70, 80, 90, 100, 105, 110, 120, 130, 140, 150, 160, 170, 196};  // Note the endpoints and the midpoint are included
const int num_dists = sizeof(dists) / sizeof(int);

unsigned long now = millis();
unsigned long last = now;
int time_since_last = 0;

const int num_measurements = 20;


void setup() {
  delay(50);
  Wire.begin();             // Begin I2C communication
  delay(50);
  Serial.begin(BAUD_RATE);  // Begin serial connection
  delay(50);

  Serial.println("Sensor calibration");

  sensor.setTimeout(250);
  while (!sensor.init()) {
    Serial.println("Failed to detect and initialize sensor VL53L0X!");
    delay(1000);
    }

  // Set sensor timing budget, in microseconds (20000 is the minimum)
  sensor.setMeasurementTimingBudget(20000);
  sensor.startContinuous();

  servo.attach(SERVO_PIN);  // Attach servo object
  delay(500);

  servo.writeMicroseconds(SERVO_CMD_REST);

  Serial.print("\n");
  Serial.print("BEGIN DATA COLLECTION\n");
  delay(1000);

  for (int i = 0; i < num_dists; i += 1) {
//    int dist_cur = map(i, 0, num_steps, dist_min, dist_max);
    int dist_cur = dists[i];
    Serial.print("True distance ");
    Serial.print(dist_cur);
    Serial.print("\n");

    delay(10000); // This wait time is for you to move the ball to the new position. Modify as needed.

    for (int count = 1; count <= num_measurements; count += 1) {
      // Get a new sensor reading
      int reading = sensor.readRangeContinuousMillimeters();
      Serial.println(reading);
      delay(100);
    }
    delay(500);
    Serial.print("\n");
  }
  Serial.print("END DATA COLLECTION\n");
}


void loop() {
  delay(1);
}


int read_int() {
  int val;
  unsigned char serial_buffer[INT_SIZE];
  if (Serial.readBytes(serial_buffer, INT_SIZE) == INT_SIZE)
    memcpy(&val, serial_buffer, INT_SIZE);
  else
    val = SERVO_CMD_REST;
  return val;
}

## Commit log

2021-07-06 edit parts list
    [parts_list.xlsx]
2021-08-24 Reorganize, improve servo & sensor calibration
    [parts_list.xlsx, vl53l0x_variance.xlsx]
2021-08-29 Add interface.ino Arduino sketch & support files
2022-04-11 Reorganize, update parts list
    [parts_list.xlsx]
2022-04-20 Replace settings.py with a YAML configuration framework
2022-04-21 Update configuration framework for ease of use
2022-04-22 Add CAD
    [base_hinge_fork.prt, base_hinge_fork.stp, fork.prt, fork.stp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]
2022-04-27 Add interface_headless
    Attempt to eliminate Arduino TX bug when operating without serial connection
2022-05-09 Add full assembly CAD
    [arduino_box.prt, backstop.prt, ball.prt, base.prt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]
2023-06-04 Use constant setpoint in arduino api
